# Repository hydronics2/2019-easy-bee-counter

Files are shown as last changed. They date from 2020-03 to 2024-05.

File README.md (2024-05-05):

# 2019 Easy Bee Counter V.1

This version of the bee counter is easy to solder and assemble (all through-hole).  It's been tested and works* with sample code provided.

The current tested design is easy to program and approachable to beginner programmers.  The printed circuit board accepts multiple Arduino platforms made by Adafruit including their line of [Adafruit Feather](https://www.adafruit.com/category/777) type micro-controllers and [Adafruit ItsyBitsy](https://www.adafruit.com/category/1008) micro-controllers.   The Adafruit feathers include wifi and long range radio features (*~~esp8266~~, esp32, and **LoRA). All the ItsyBitsy 3V models (M0, M4, and 32u4) should work fine.

*the esp8266 is missing A5 so you have to jumper to another pin
**see below issue with SPI

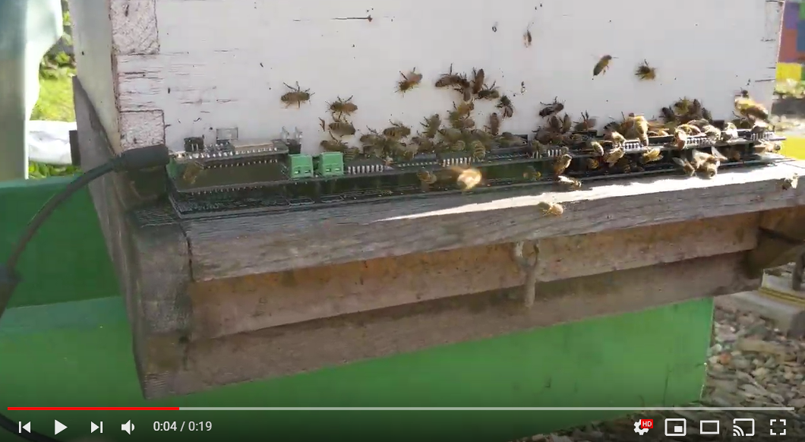
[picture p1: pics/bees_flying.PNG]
Foo (https://youtu.be/SzXWWUh2k8w)


### [Data Analysis - *why count bees?](https://github.com/hydronics2/2019-easy-bee-counter/blob/master/Data/README.md)
### [Instructions](https://github.com/hydronics2/2019-easy-bee-counter/blob/master/instructions/README.md)
### [Arduino Code](https://github.com/hydronics2/2019-easy-bee-counter/blob/master/arduino/README.md)
### Major Differences/Improvements
- All through-hole components for easy soldering
- Dual footprint, socketed, off-the-shelf micro-controllers => Feather and ItsyBitsy
- Program in Arduino, Lua, and microPython
- A total of 24 gates, 48 sensors, 6 shift registers
- ~14.75" long stretching the entire opening of a langstroth hive for easy placement
- using 2 PCBs to create a sandwich is an inexpensive quick solution. The PCBs must be ordered [black](https://github.com/hydronics2/2019-easy-bee-counter/tree/master/instructions/ordering_instructions) so the IR LED emitter is absorbed into the material.
- using 6 pin headers to create the turn-styles or gates
- N-Ch mosfet controlled IR LEDs such that LEDs can be controlled ON for short periods during while sensing (~75us). Allows for reduced power to less than 1ma (plus micro-controller).
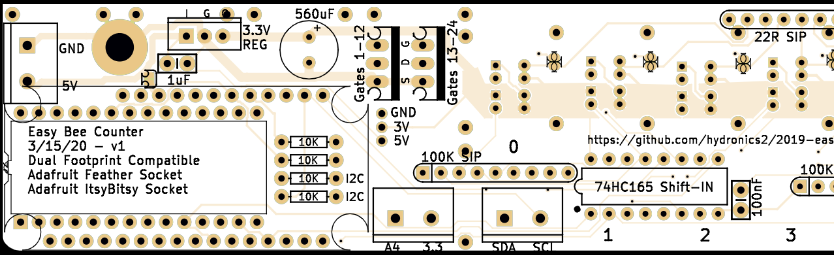
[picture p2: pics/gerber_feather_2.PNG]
feather

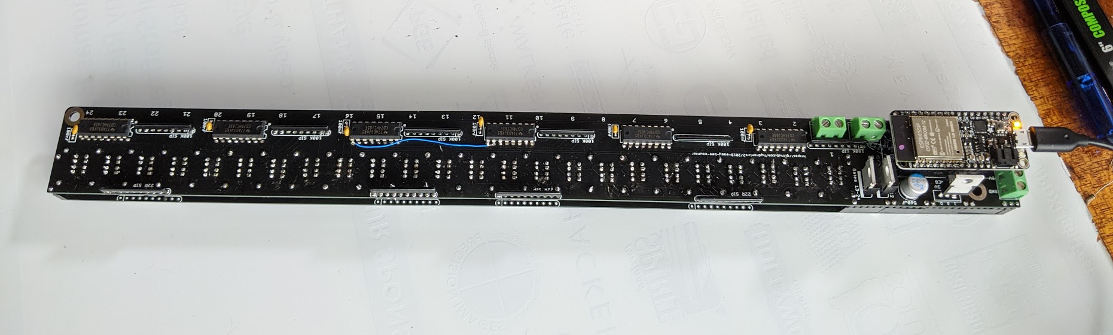
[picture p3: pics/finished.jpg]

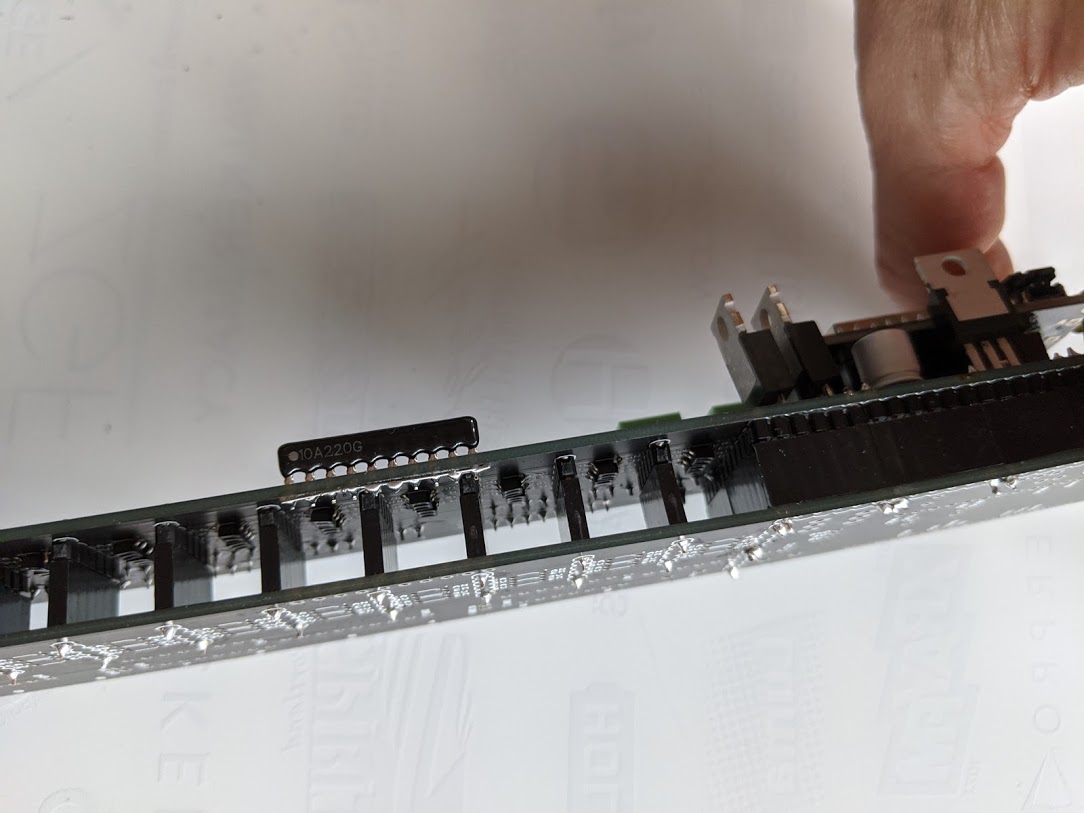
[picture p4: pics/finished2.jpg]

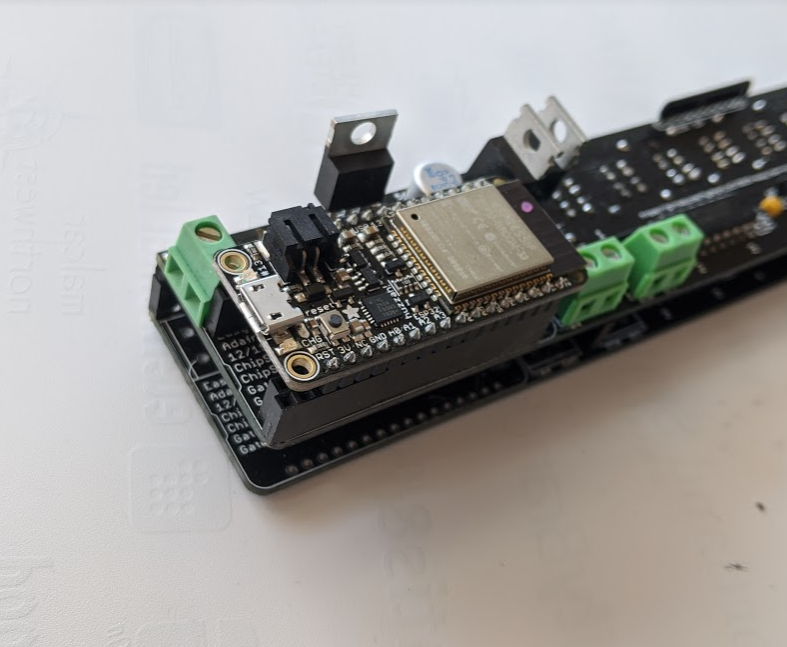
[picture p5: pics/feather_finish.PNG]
feather

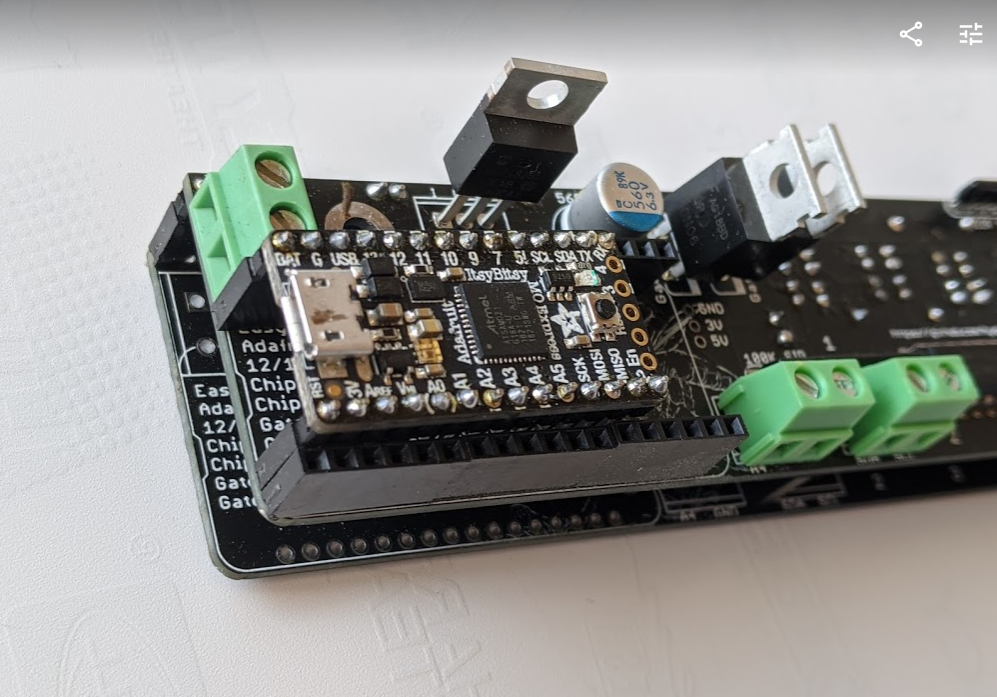
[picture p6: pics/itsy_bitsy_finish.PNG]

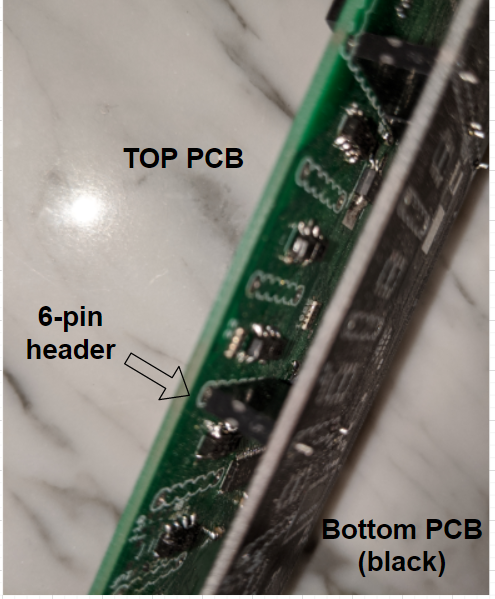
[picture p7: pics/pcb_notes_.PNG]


### General Operation
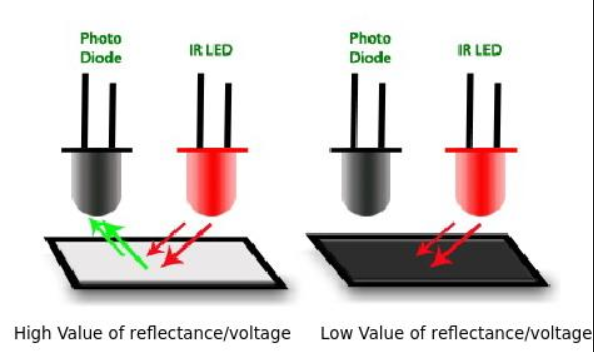
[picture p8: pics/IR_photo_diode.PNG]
https://github.com/hydronics2/2019-easy-bee-counter/blob/master/pics/IR_photo_diode.PNG
Honeybees are forced through 24 gates where optical sensors (48 sensors) determine whether the bee is present and determine the direction of the bee movement. Each optical sensors has an IR LED and an IR sensor. If no bee is present the IR light is absorbed into the black surface. If a bee is present the IR light reflects off the bee and triggers the sensor. 

### Micro-Controller Pinout
#### Feather ESP32 Pinout
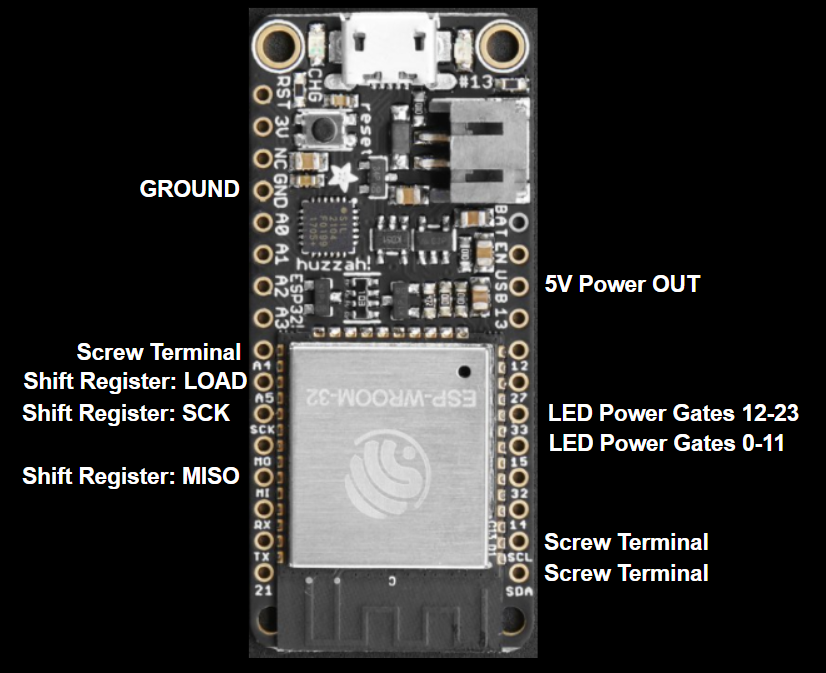
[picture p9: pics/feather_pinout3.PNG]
feather

#### ItsyBitsy Pinout
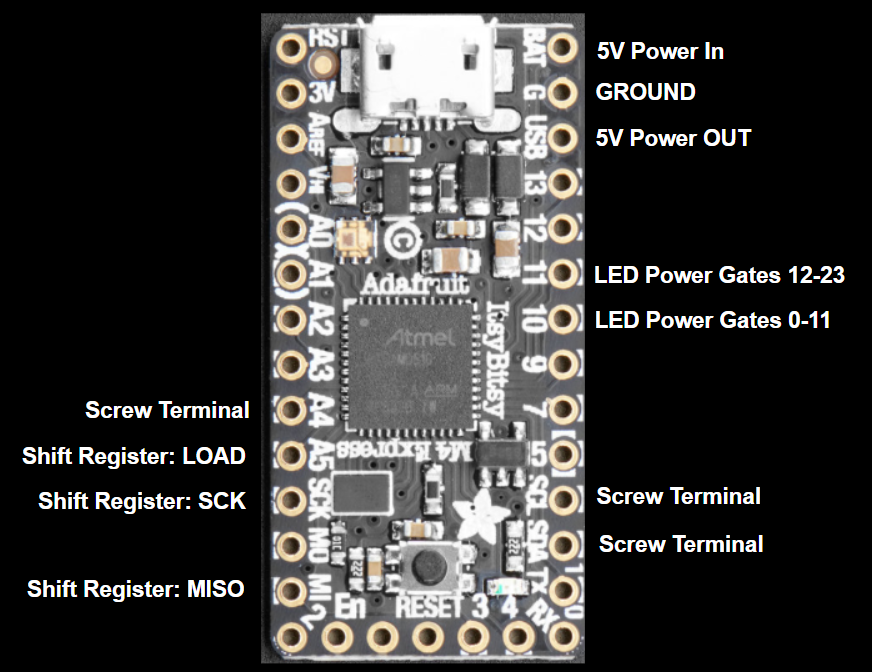
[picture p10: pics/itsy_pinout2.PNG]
itsy

### Shift-in registers
There are 6 shift-in registers. Here's a great description for how to connect and program [shift registers](http://www.gammon.com.au/forum/?id=11979).  The micro-controller's SPI pins read the shift registers. All six shift registers are read at the same time. The sensors are normally pulled low and show 3.3V or HIGH when a transistor is triggered and a bee is present.

Unfortunately the shift registers we're using (the most popular shift register chip!) are not [full SPI devices](https://electronics.stackexchange.com/questions/121249/how-to-put-a-74hc165-on-an-spi-bus) and wont share the SPI with other devices.. They're like the worst SPI devices!... therefore some boards like the Adalogger or LoRa just wont work out of the box. You can still do it by cutting some traces and patching the SPI lines to free pins and bitbanging the SPI to the shift registers.. buy yeah not optimum. You can get a true-spi shift register but the pinout will be different than the 74hc165 used here.

### IR LEDs
The 48 LEDs are divided into two sets of 24 with each set controlled by an N-ch mosfet. The normal forward voltage of each IR LED is 1.2V and about 20ma as shown on the [data sheet](https://www.sparkfun.com/datasheets/Robotics/QR_QRE1113.GR.pdf). Two LEDs are connected in series with a 22ohm resistor. There are jumpers on the board that allow the LEDs to bypass the current limiting resistors. Do not solder the jumper until fully tested! Refer to [these instructions](https://github.com/hydronics2/2019-easy-bee-counter/tree/master/instructions)

### Power
The PCB design connects the USB power pin from the uController to the 3.3V regulator so that a usb cable connected to the micro-controller can power the entire project.

### Bill of Materials
#### uController
The code was tested with the feather esp32 Huzzah and itsyBitsy M0 but will work with all these boards.
- feather Huzzah from [mouser](https://www.mouser.com/ProductDetail/485-3591)
- feather esp8266 from [mouser](https://www.mouser.com/ProductDetail/485-2821)
  - the esp8266 is missing A5, so if this micro is used you have to jumper to another pin
- feather LoRa 900mhz from [mouser](https://www.mouser.com/ProductDetail/485-3178)
- ItsyBitsy M0 from [mouser](https://www.mouser.com/ProductDetail/485-3727)
- ItsyBitsy M4 from [mouser](https://www.mouser.com/ProductDetail/485-3800)
#### PCB
[JLCPCB](https://jlcpcb.com/quote#/) ~$16-25 with shipping. Order the PCBs Black. See [these instructions](https://github.com/hydronics2/2019-easy-bee-counter/tree/master/instructions/ordering_instructions) for ordering.
#### Parts and Pieces from [mouser](https://www.mouser.com/ProjectManager/ProjectDetail.aspx?AccessID=054286973a)
See alternative pricing below for cheaper options specifically for the reflectance sensors.
- [qre1113 Reflective Sensors](https://www.mouser.com/ProductDetail/512-QRE1113f) qty(48)
- [6 pin female headers](https://www.mouser.com/ProductDetail/437-8018700610001101) 7mm high, 0.1" spacing, qty(~36)
- [22ohm resistors](https://www.mouser.com/ProductDetail/Xicon/266-22-RC?qs=sGAEpiMZZMvrmc6UYKmaNXFefT4dxyTCwtpTxTI0yoo%3D), bussed, qty(4)
SIP Packaged, bussed
- [100k ohm resistors](https://www.mouser.com/ProductDetail/IRC-TT-Electronics/L091S104LF?qs=sGAEpiMZZMvrmc6UYKmaNdnTrsZX%2FuSiyGduauH5Qpc%3D) bussed, qty(6)
SIP-9, 8 resistors, 9 pins
- Shift registers, qty(6)
[74HC165](https://www.mouser.com/ProductDetail/595-SN74HC165N)
- [3.3V Regulator](https://www.mouser.com/ProductDetail/Microchip-Technology/MCP1826S-3302E-AB?qs=sGAEpiMZZMsGz1a6aV8DcJ7KfjtCj7Xd5CqQpyOghgk%3D), (input, ground, output - IGO, pinout), qty(1)
- [screw terminals](https://www.mouser.com/ProductDetail/490-TB006-508-02BE) Two pin, 0.1", qty(3)
- [0.1 uF Ceramic Capacitor](https://www.mouser.com/ProductDetail/594-K104K15X7RF53H5), through hole, qty(6)
- [1 uF Ceramic Capacitor](https://www.mouser.com/ProductDetail/594-K105Z20Y5VF5TL2), through hole, qty(1)
- [560uF, 6.3V Capacitor](https://www.mouser.com/ProductDetail/661-APSC6R3L561MH08S)
low esr, 3.5mm lead spacing, 8mm diameter
- N-Channel Mosfet [FQP30N06](https://www.mouser.com/ProductDetail/512-FQP30N06L), qty(2)
  - [chinswain](https://github.com/hydronics2/2019-easy-bee-counter/issues/20#issuecomment-2094117078) suggested using this IRLB8721PbF N-Channel mosfet. He suggested the signal threshold of 3.3V was not sufficient to meet the gate threshold for the FQP30N06L... and it could be the ebay versions of the FQP30N06L floating around are not to spec.

#### Alternative pricing from Chinese distributor LCSC
Someone pointed out some alternative pricing that can really bring the cost down.
- [ITR8307 Reflectance Sensors](https://lcsc.com/product-detail/Photo-Interrupter_Everlight-Elec-ITR8307_C63451.html) ~$0.13/each @ qty(48) (same as QRE1113)
- [6 pin female headers](https://lcsc.com/product-detail/Pin-Header-Female-Header_BOOMELE-Boom-Precision-Elec-C40877_C40877.html) 8.5mm high. ~$0.05/each @ qty(36+)
- [22 ohm SIP](https://lcsc.com/product-detail/Resistor-Networks-Arrays_FH-Guangdong-Fenghua-Advanced-Tech-A09-220JP_C9105.html) 8 resistor, 9 pin, it will fit. $0.44 for qty(4)
- [100k SIP Resistors](https://lcsc.com/product-detail/Resistor-Networks-Arrays_FH-Guangdong-Fenghua-Advanced-Tech-A09-104JP_C9108.html) 8 resistor, 9pin, it will fit. $0.44 for qty(6)

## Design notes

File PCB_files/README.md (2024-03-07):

## Printed Circuit Board (PCB)

This PCB version has two footprints that accept the wider (0.8") Adafruit Feather micro-controllers such as the [esp32](https://www.adafruit.com/product/3405) and the narrower (0.6")[Adafruit ItsyBitsy](https://www.adafruit.com/category/1008) micro-controllers.

**UPDATE** The GERBER files were developed from the kicad board files so had to remove the gerber files. You now have to use the Eagle board files or generate gerber files from the eagle board files.... or a lot of PCB manufacturers will take eagle PCB files and you don't have to generate your own gerber files. You can still use the kicad files but you have to route a small trace for the SCK pin. See this bug report: https://github.com/hydronics2/2019-easy-bee-counter/issues/25 

feather

These files were created in Autocad EAGLE PCB software. The zipped files are the gerber files needed by the PCB manufacturer.

Right click and 'save link as' to download the files and then upload them to the PCB manufacturer. See the [ordering instructions here](https://github.com/hydronics2/2019-easy-bee-counter/tree/master/instructions/ordering_instructions). Most board shops require a minimum order of 3-5 boards and you'll need 2 boards to sandwich together to complete one bee counter.

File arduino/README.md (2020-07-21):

# Arduino

There are three arduino scripts attached.
- Blink_IR_leds.ino - used to visually inspect LEDs working
- test_shift_registers.ino - used to functionally test sensors
- bee_counting.ino - used to count bees!

### Warning
Soldering the 24 jumpers increases the throw range of the IR sensors by increasing the forward voltage and current in the LED. This is fine if we keep the LEDs ON time to less than 100us. This is described in the [data sheet](https://www.sparkfun.com/datasheets/Robotics/QR_QRE1113.GR.pdf).

Two scripts above, both [test_shift_registers](https://github.com/hydronics2/2019-easy-bee-counter/blob/master/arduino/test_shift_registers/test_shift_registers.ino) and [bee_counting](https://github.com/hydronics2/2019-easy-bee-counter/blob/master/arduino/bee_counting/bee_counting.ino) satisfy this requirement by only turning the LEDs ON for 75us.  This is shown on line 68 (shift register) and line 158 (bee_counting). Following the ON time there is a delay of ~15-20ms before turning them ON again which preserves the life of the LED.

### Calibrating the Bee Counter
I've captured some amazing data over the years. It's possible to calibrate the bee counter to achieve the required repeatability. Some of the obstacles to calibrate for include:
 - although bees don't add propolis to sensors they will spend several days filling voids with propolis upon initial installation
 - bearding in the summer evenings and general guard bees mulling about give false triggers
 - direct sun light at a low angle will false trigger sensors (this can be mitigated pretty easily)

One method is to measure the speed of the bees movement and only count known movements and throwing out all false triggers. This method misses a lot of bees but can give consistent values. It takes a bee about 180-350ms to traverse the sensor region.

The [bee_counting](https://github.com/hydronics2/2019-easy-bee-counter/blob/master/arduino/bee_counting/bee_counting.ino) code measures the speed of the bees through the sensor and counts bees moving faster than 650ms and demands the time between finishing one sensor and finishing the 2nd sensor is less than 150ms.

### Micropython

@jin4 contributed the python code that ran successfully on a pycom device... "This code runs on a pycom device, but i think the code will work on any micropython device since the imports are not pycom specific."

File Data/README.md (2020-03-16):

# Possible Uses
- the rate of expansion or decline of bee flights might indicate hive health
- the expansion or decline of orientation flights over days might signal queen health
- the time shift between peaks of bees leaving and returning might indicate number of foragers and distance to pollen/nectar source.
- comparison between two or move hives to test for manipulations; such as,
  - adding/removing honey supers
  - internal sugar syrup feeding
  - oxalic acid mite treatments
- honey bee education or museum type installation
- introduction to electronics, soldering and micro-controller programming

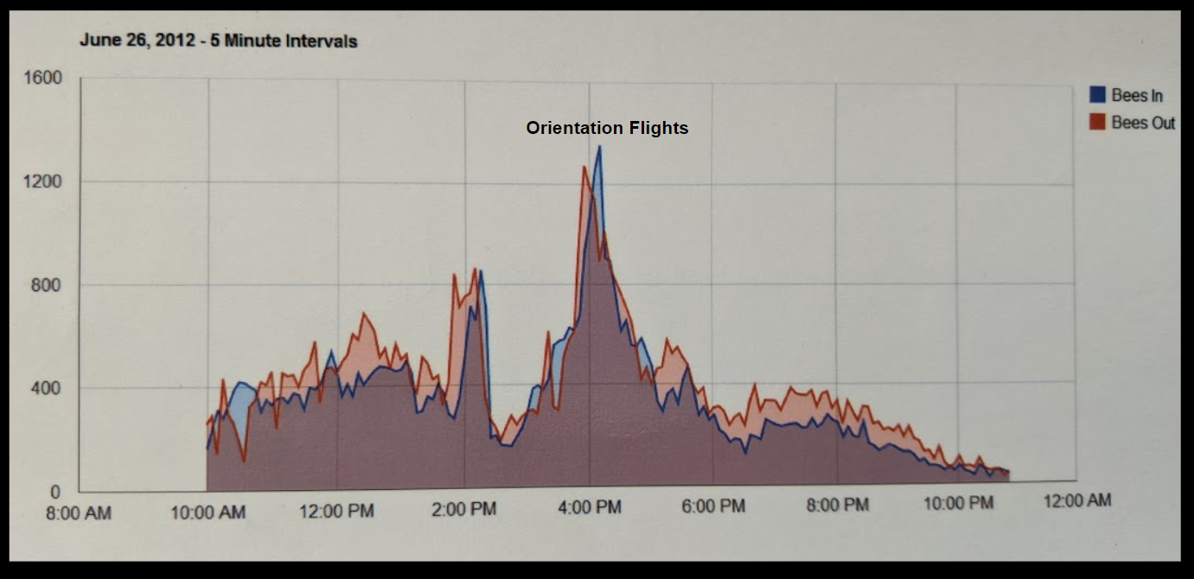
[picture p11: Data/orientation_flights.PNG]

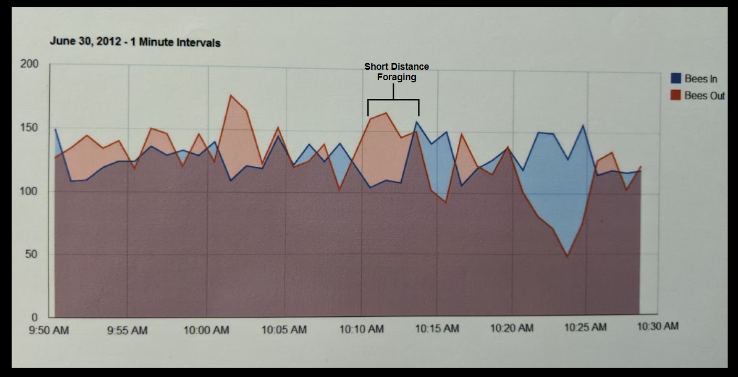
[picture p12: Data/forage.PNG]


## Hive health
Equating bee flight data and orientation flights to over all hive health or queen health seems possible. Orientation flights is a behavior of 'middle aged' bees about [20 days old](https://www.arnia.co.uk/honey-bee-orientation/#). Before foraging bees of this age will leave the hive as a group at around mid day resulting in an easy to see ~45min peak in data.

If there is a drop in orientation flights it might indicate a reduction in egg laying ~42 days prior (22 days hatch + 20 days till forage).

## Foraging distance
It's easy to see small but distinct shifts between bees OUT and bees IN. This indicates both a volume of bees that are leaving and returning together as well as a rough distance or time to the foraging location.

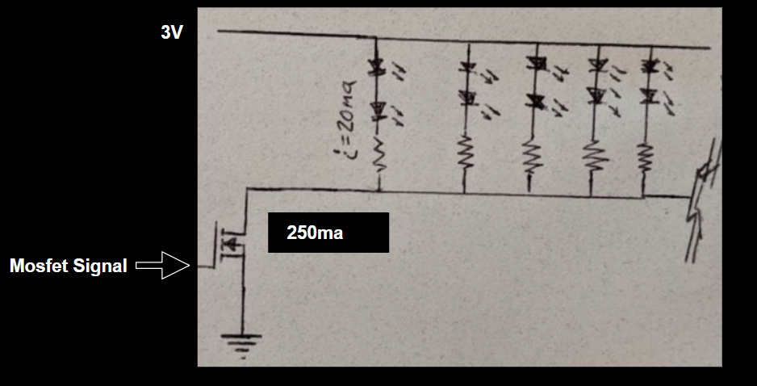
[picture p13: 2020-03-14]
pics/led_schematic.PNG

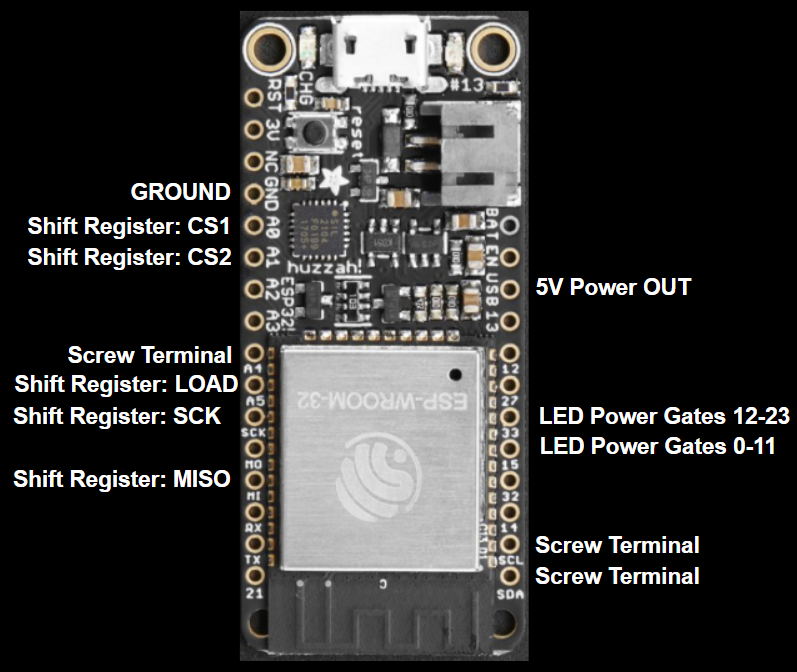
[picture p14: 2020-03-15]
pics/feather_pinout2.PNG

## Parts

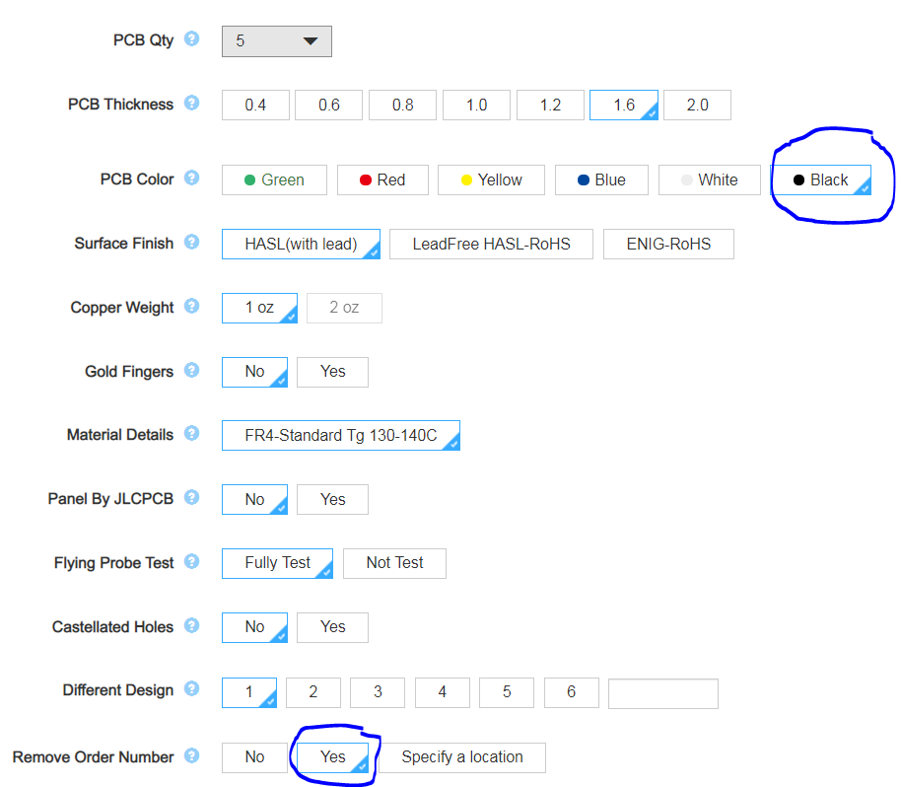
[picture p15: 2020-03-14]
pics/JLCPCB_order.PNG

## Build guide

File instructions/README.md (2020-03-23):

# 2019 Easy Bee Counter V.1 Build Instructions

This version of the bee counter is all through hole components. It's easy to solder and assemble. This is the 2nd version of the board (V1) completed March 2020. If you got the [Version 0](https://github.com/hydronics2/2019-easy-bee-counter/tree/b06d461f1881f2709d81f82d817dc76170a77fa7) board (Jan/Feb 2020) you just have to fix some of my previous mistakes including adding a jumper wire shown [here](https://github.com/hydronics2/2019-easy-bee-counter/blob/master/instructions/archive)

1) Install IR sensors - [QRE1113](https://www.mouser.com/ProductDetail/512-QRE1113f) or [ITR8307](https://lcsc.com/product-detail/Photo-Interrupter_Everlight-Elec-ITR8307_C63451.html)

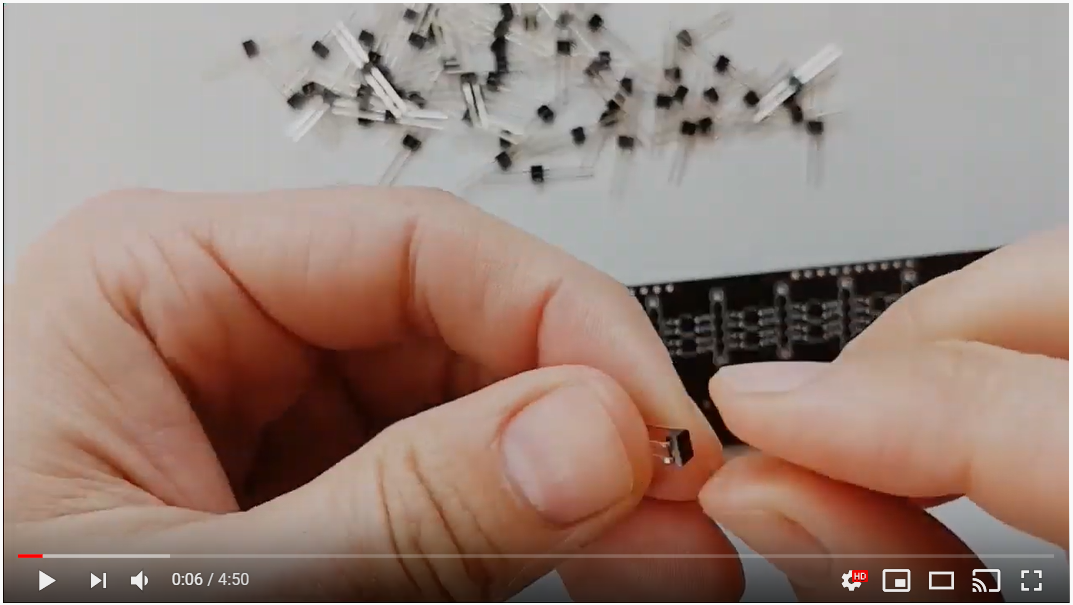
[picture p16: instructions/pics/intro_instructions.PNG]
(https://youtu.be/Xx23OmlHwkE)


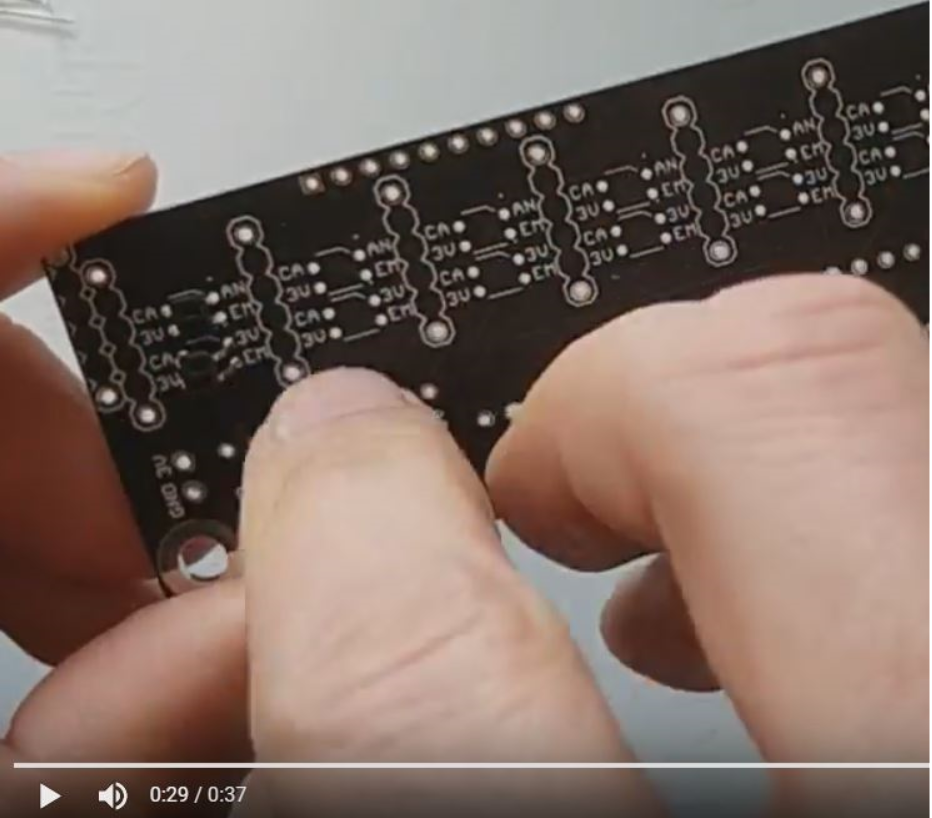
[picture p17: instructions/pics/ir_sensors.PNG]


2) install shift registers qty(6), SIP 22R LED resistors and 100k pulldown resistors.
- Shift registers, qty(6) [74HC165](https://www.mouser.com/ProductDetail/595-SN74HC165N)
- [22ohm resistors](https://www.mouser.com/ProductDetail/Xicon/266-22-RC?qs=sGAEpiMZZMvrmc6UYKmaNXFefT4dxyTCwtpTxTI0yoo%3D), bussed, qty(4)
SIP Packaged, bussed
- [100k ohm resistors](https://www.mouser.com/ProductDetail/IRC-TT-Electronics/L091S104LF?qs=sGAEpiMZZMvrmc6UYKmaNdnTrsZX%2FuSiyGduauH5Qpc%3D) bussed, qty(6)
SIP-9, 8 resistors, 9 pins

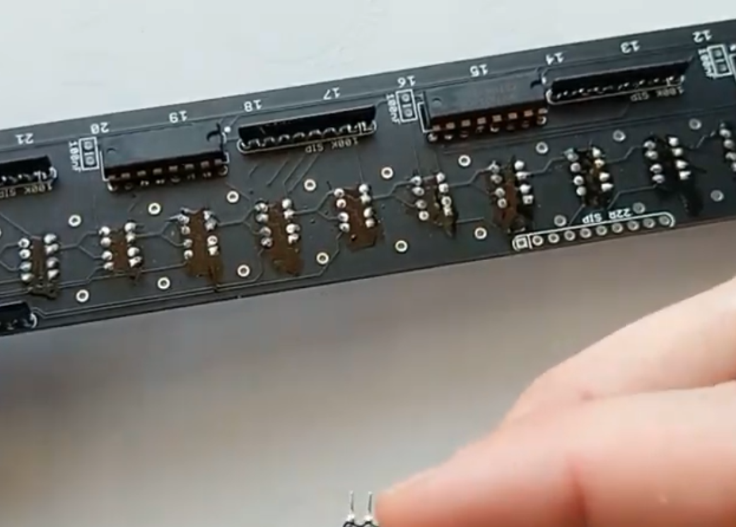
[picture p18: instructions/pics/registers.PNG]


3) install power mosfets qty(2),
- N-Channel Mosfet [FQP30N06](https://www.mouser.com/ProductDetail/512-FQP30N06L)

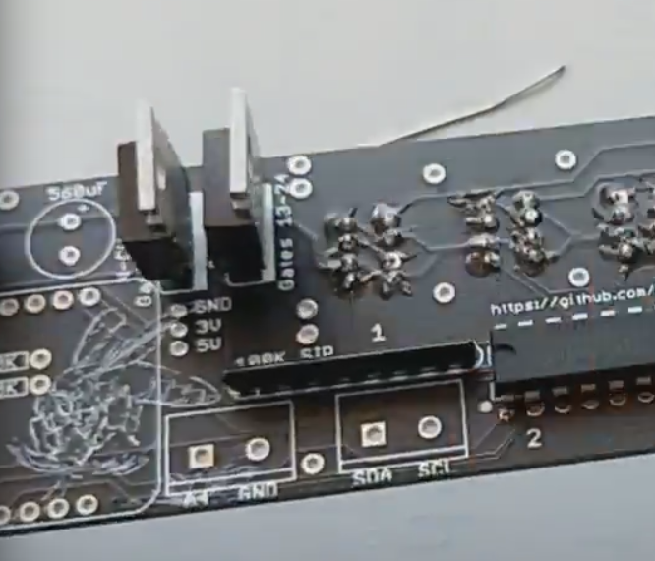
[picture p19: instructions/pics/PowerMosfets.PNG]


4) install small capacitors

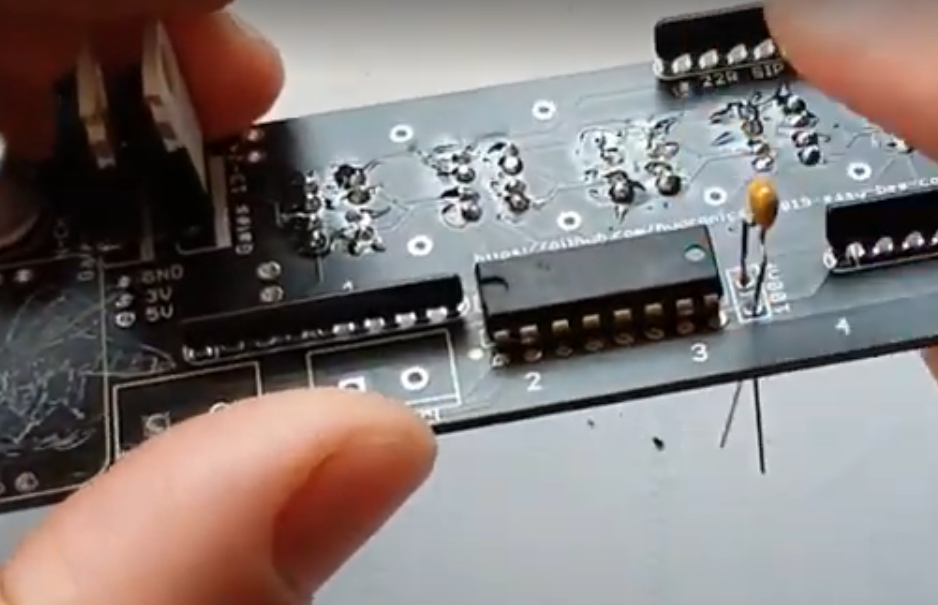
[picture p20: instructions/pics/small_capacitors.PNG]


5) place/solder 3.3V power regulator

- [3.3V Regulator](https://www.mouser.com/ProductDetail/Microchip-Technology/MCP1826S-3302E-AB?qs=sGAEpiMZZMsGz1a6aV8DcJ7KfjtCj7Xd5CqQpyOghgk%3D), (input, ground, output - IGO, pinout), qty(1)

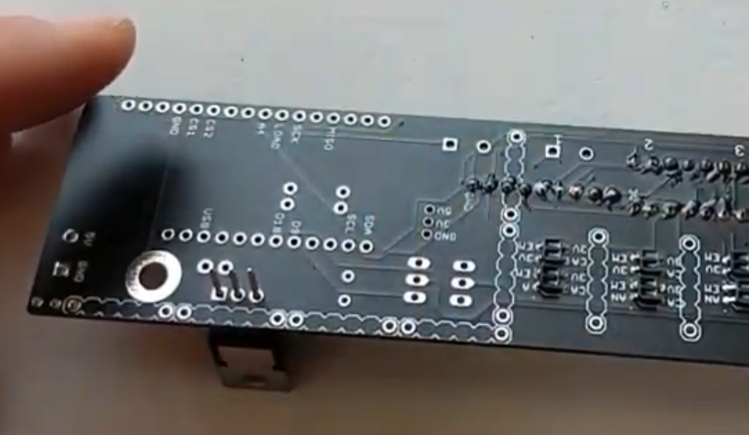
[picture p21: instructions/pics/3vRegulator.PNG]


6) install large Capacitor

- [560uF, 6.3V Capacitor](https://www.mouser.com/ProductDetail/661-APSC6R3L561MH08S)

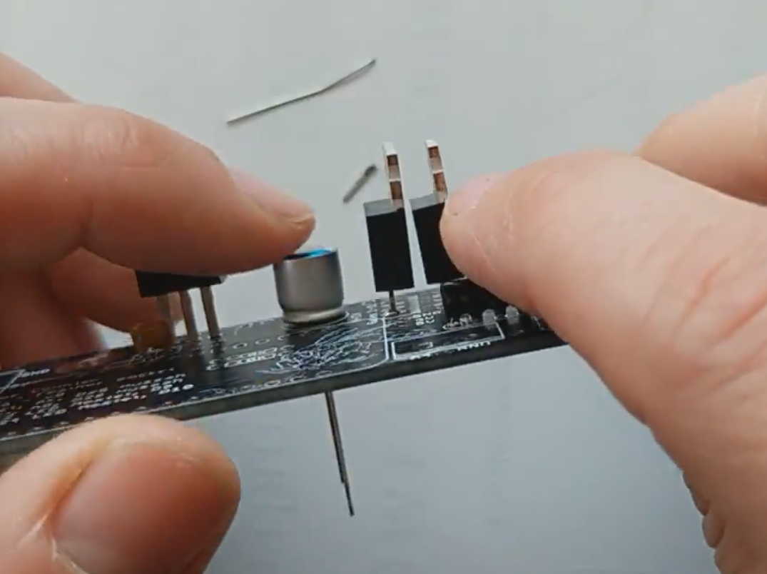
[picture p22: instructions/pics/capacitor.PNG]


7) install green screw terminals, qty(3)

- [screw terminals](https://www.mouser.com/ProductDetail/490-TB006-508-02BE) Two pin, 0.1", qty(3)

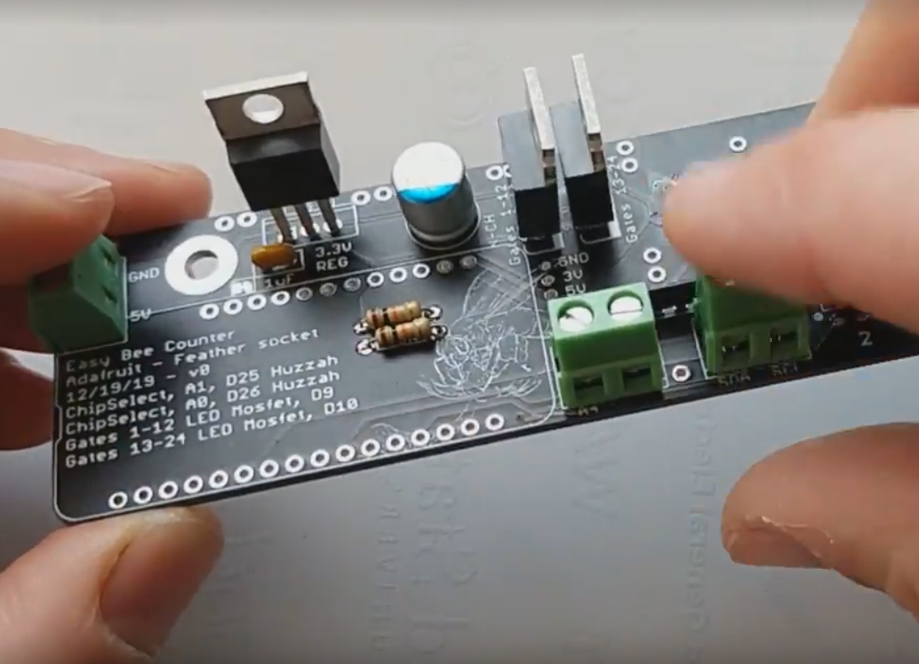
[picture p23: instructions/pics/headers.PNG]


8) install headers for microprocessor

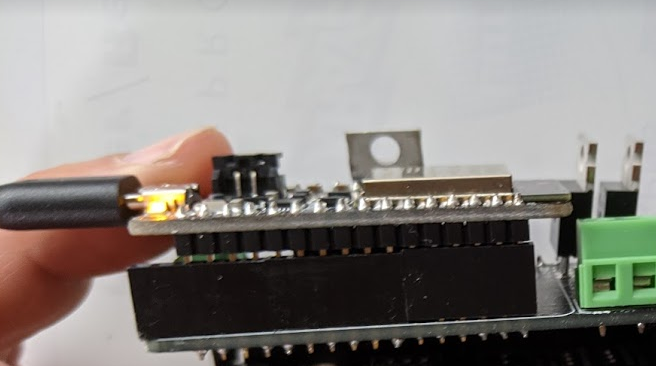
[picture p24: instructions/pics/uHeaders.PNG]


9) install qty(4) 10K Resistors (picture is wrong.. only shows 2 resistors)
- i2c pullup resistors
- pulldown resistors for power mosfets

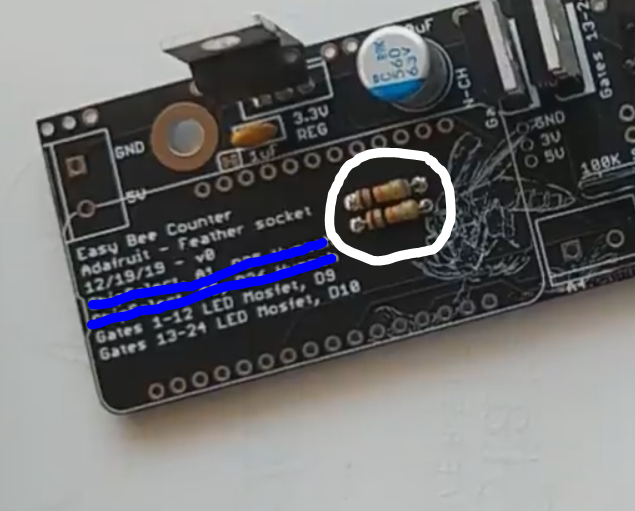
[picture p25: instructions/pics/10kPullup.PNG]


## TEST sensors
Before you go any farther, test all your LEDs/sensors! It's much easier to test these now before going further.
Run the sample code [blink_IR_Leds](https://github.com/hydronics2/2019-easy-bee-counter/blob/master/arduino/Blink_IR_Leds/Blink_IR_Leds.ino).

The IR LEDs are invisible to the human eye but many phones and cameras allow you to see the IR LEDs. See picture. (unfortunately most iphones have IR filters so try another phone until you see IR leds). This step is very important so make sure you can see all the LEDs.

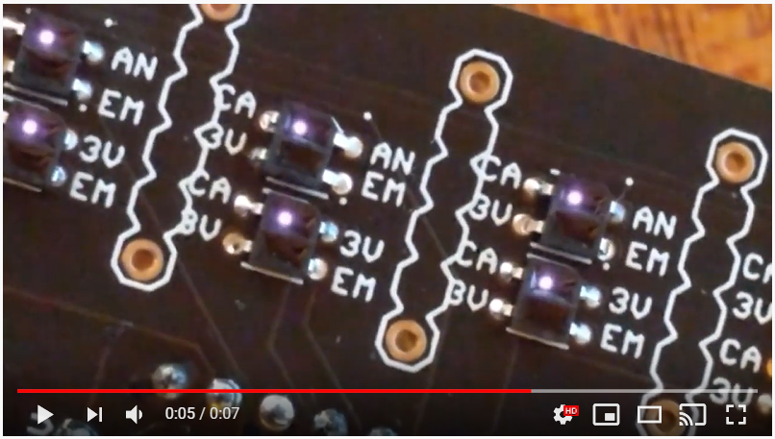
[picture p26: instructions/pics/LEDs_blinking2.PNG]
(https://youtu.be/hH9fQr7Om6E)


LEDs look good? If no LEDs are blinking? Check to make sure you have 3.3V on the 3.3V pin header. If one or two LEDs are out, reflow your pins and/or replace the LEDs until you get 100% LEDs blinking together.

LEDs good, great, next test the shift registers with the sample code [test_shift_registers](https://github.com/hydronics2/2019-easy-bee-counter/blob/master/arduino/test_shift_registers/test_shift_registers.ino). Use a white piece of paper to trigger the sensors. If some sensors are not working, check your pins, heat up and reflow solder on pins as needed.

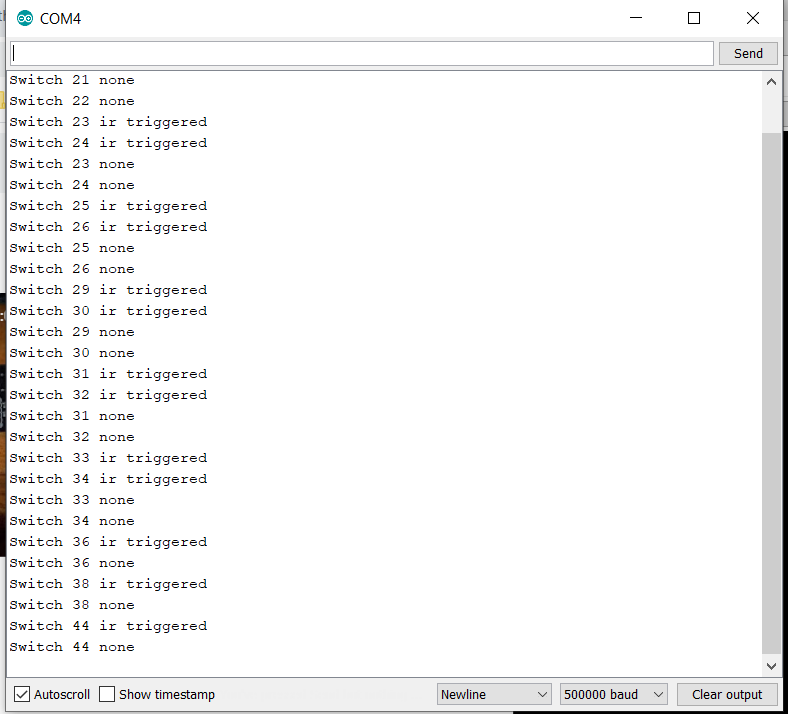
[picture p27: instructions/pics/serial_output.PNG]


10) Finish assembly once all sensors are tested. Install the headers that connect the top PCB to the bottom PCB.

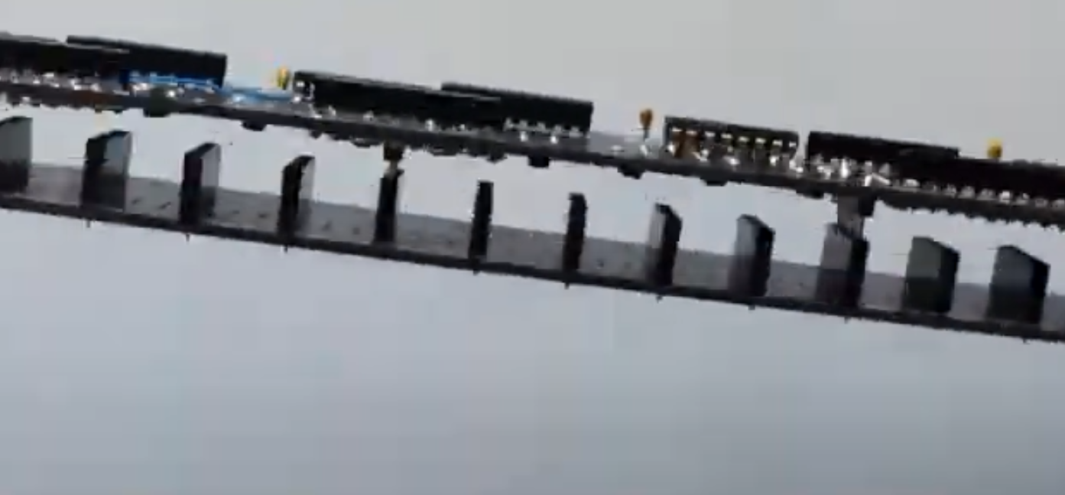
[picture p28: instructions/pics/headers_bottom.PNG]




11) Ok, once everything is tested out, you can solder these jumpers.... Soldering the 24 jumpers increases the throw range of the IR sensors by increasing the forward voltage and current in the LED. This is fine to do if we keep the LEDs ON time to less than 100us.

Two scripts provided, both [test_shift_registers](https://github.com/hydronics2/2019-easy-bee-counter/blob/master/arduino/test_shift_registers/test_shift_registers.ino) and [bee_counting](https://github.com/hydronics2/2019-easy-bee-counter/blob/master/arduino/bee_counting/bee_counting.ino) satisfy this requirement by only turning the LEDs ON for 75us.  This is shown on line 68 (shift register) and line 158 (bee_counting).

Solder all 24 of the jumpers.
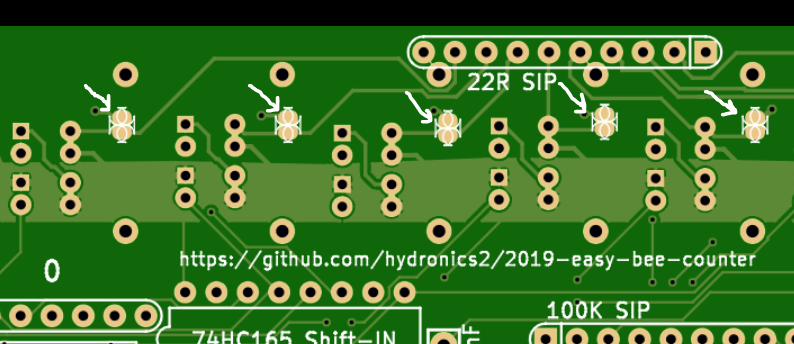
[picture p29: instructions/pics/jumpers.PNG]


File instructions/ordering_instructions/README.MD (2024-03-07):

## Ordering from JLCPCB

There are a lot of different PCB manufacturers to choose from. These instructions show JLCPCB. You need a manufacturer that can make black PCBs if you want to use the PCBs to make a sandwich. The IR LEDs/sensors need to point to a black surface to prevent false triggers, so the bottom PCB has to be black.

1. Download the entire repo... hit the large green button that says "clone or download" [github](https://github.com/hydronics2/2019-easy-bee-counter)... navigate to the Eagle_v0.2 file. These are the PCB files. Do not use the kiCad files as there is a missing trace for the SCK pin for the itsybitsy footprint.
2. Go to [JLCPCB.com](https://jlcpcb.com/quote#/), create an account and click the ORDER NOW button.
3. Add your PCB files.
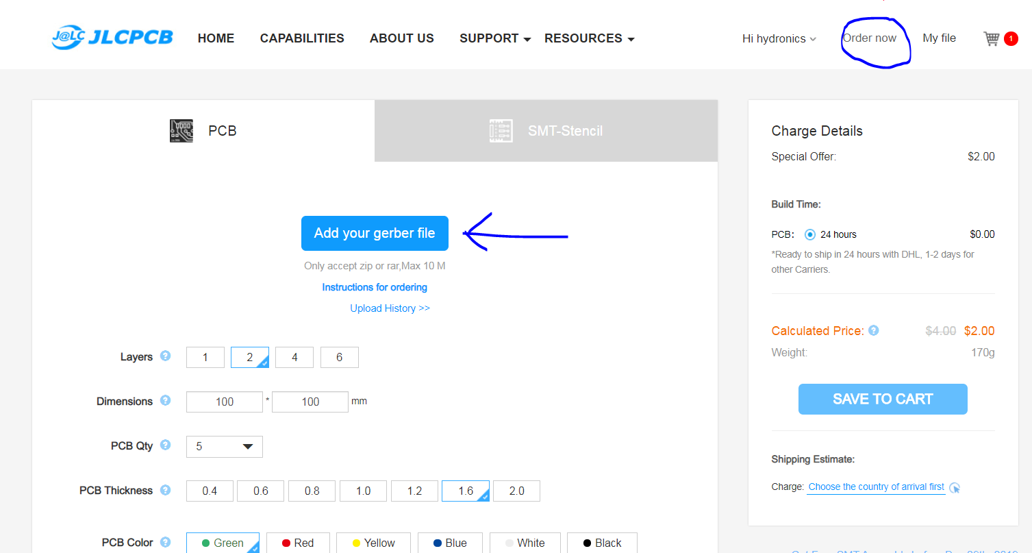
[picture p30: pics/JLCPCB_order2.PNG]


4. Select 'Black' as the PCB color.  Also for "Remove Order Number", select YES
[pic](https://github.com/hydronics2/2019-easy-bee-counter/blob/master/pics/JLCPCB_order.PNG)

The cost is about $8 for a minimum order of qty(5) PCBs plus $9-16 shipping depending on method.

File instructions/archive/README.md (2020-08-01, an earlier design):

# 2019 Easy Bee Counter V.0 Build Instructions

I made a few mistakes on the first version (v0). The 74hc165 is not a true SPI device. It doesn't have a tri-state buffer on the MISO.

https://electronics.stackexchange.com/questions/121249/how-to-put-a-74hc165-on-an-spi-bus

The following fix, allows you to shift in all the data at once (all shift registers)... all shift registers are therefore always enabled. This fix wil work with all the stand alone feather micro-controllers... ESP32, ESP8266, SAMD21 M0 and M4... but doesn't work with the [LoRa module](https://cdn-learn.adafruit.com/assets/assets/000/031/658/original/feather_schem.png?1460518302) as it ALSO uses the SPI buss. In order to work with the LORa module you need to swap out the 74hc165 shift registers with true SPI based shift registers... like the 74HC589 referenced in the above [stack exchange](https://electronics.stackexchange.com/a/128220) answer.

To fix the old board... we want to read all 6 shift registers so just cut one of the MISO signal lines and add a jumper.

video cutting signal https://photos.app.goo.gl/VkyV412uJGBNS7sx8

video adding jumper https://photos.app.goo.gl/QXMhvH7FzpDfXWLs7

Top view showing cut jumper
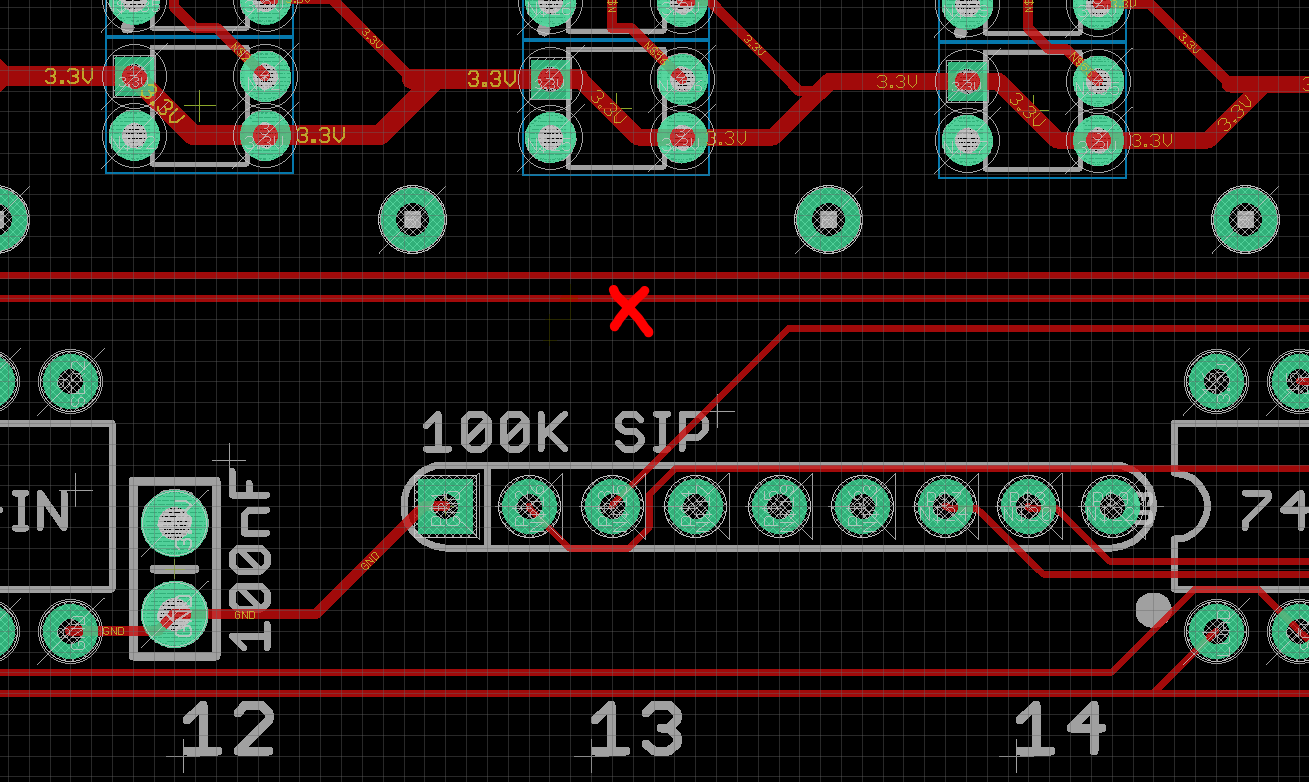
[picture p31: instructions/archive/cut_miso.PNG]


Top view showing jumper(blue)
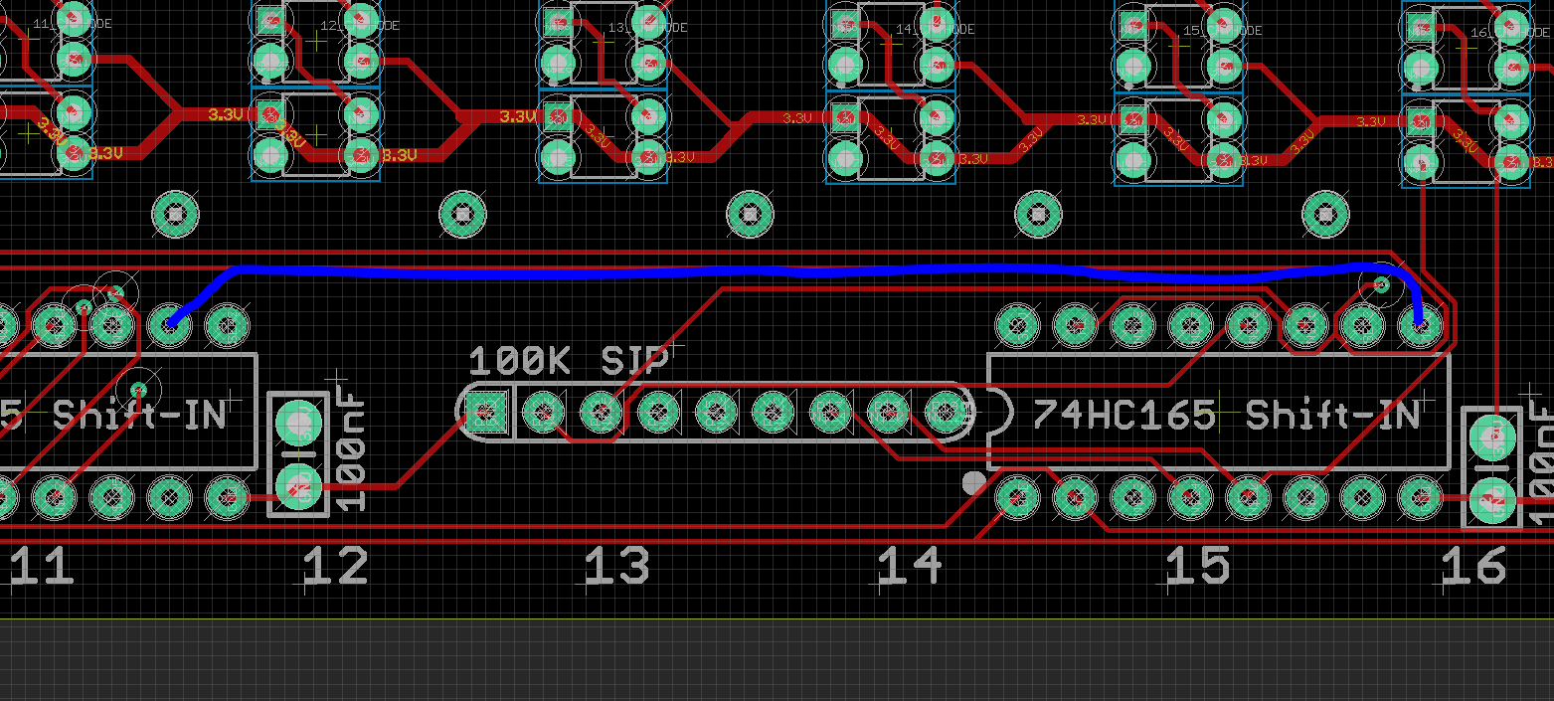
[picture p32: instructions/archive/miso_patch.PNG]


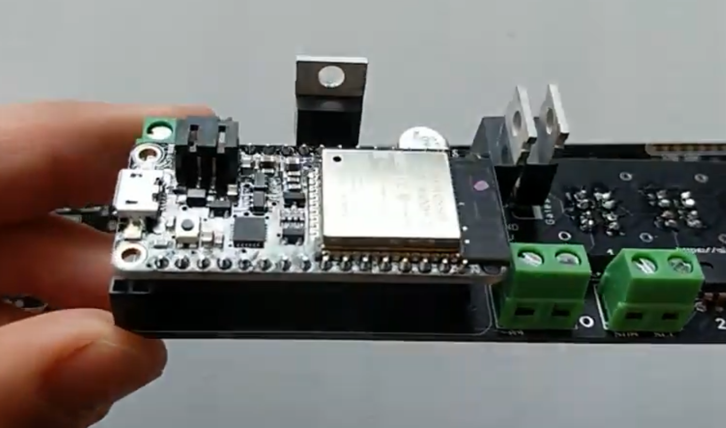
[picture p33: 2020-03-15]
instructions/pics/ucontroller_w_headers.PNG

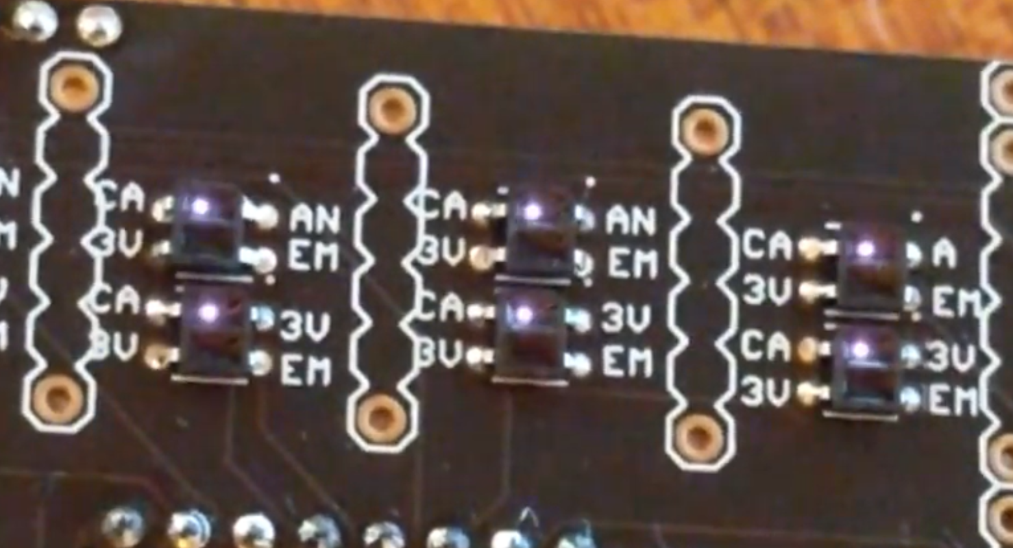
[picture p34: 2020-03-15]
instructions/pics/ir_sensors_on.PNG

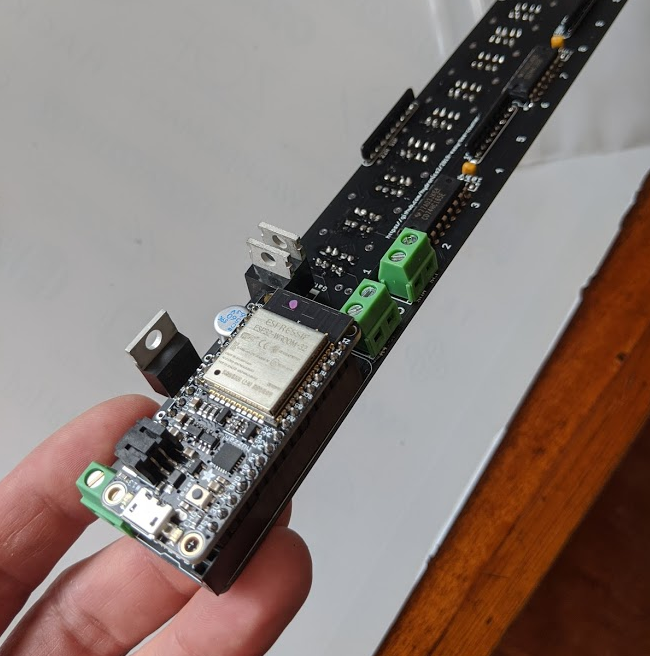
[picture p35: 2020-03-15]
instructions/pics/ucontroller_w_headers2.PNG

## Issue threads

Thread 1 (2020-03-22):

hydronics2/2019-easy-bee-counter #1: Suggestion...

owendelong, 2020-03-22:
Any reason https://recom-power.com/pdf/Innoline/R-78-1.0.pdf wouldn't be a suitable (superior) replacement for the MCP1826S-3302E-AB?

Looks like the specs are basically identical, but this is a switcher instead of a linear, so it should be more efficient (less heat dissipation, less power input, etc.

I'm looking at possibly adding some hinges and servos to the ESP32 (or ESP8266, haven't fully decided yet) version to create a programmable entrance reducer and also inputs for a load cell to track hive weight (bee and honey production, time to add supers, etc.).

I'm thinking 12, 6, 3, 2, 1 wide doors, facilitating a wide range of entrance sizes.

Curious for any thoughts you might have on this idea.

owendelong, 2020-03-23:
So looking through things, you don't actually seem to use the screw terminals for anything... Is that correct? Is the 3v,A4 screw terminal intended for connecting a load cell?

It also appears you don't actually use the I2C connections for anything. Are they needed? Am I missing something?

Thanks in advance.

BTW, love the bee logo on the board.

hydronics2, 2020-03-23:
Yes! the screw terminals are for adding sensors too. Nothing identified but that's what they are for.

I agree load cells are super important for looking at hive health and activity. 

That's an interesting idea adding retractable entrance reducers. 

you bet, I like the idea of the drop-in-replacement mini switching power supply. Especially  for say reducing parasitic losses (?).

hydronics2, 2020-03-23:
Also, If you are digging into this... I'm missing the jumpers on this CAD version. Do you follow? They are in the gerber files. They jumper the LED resistors. Just a heads up. If you already ordered the board you can easily short the SIP resistors. [That's what I did on my first version. ](https://github.com/hydronics2/2019-easy-bee-counter/blob/master/PCB_files/Eagle_v0.2/shorted_SIP_resistors.png)

owendelong, 2020-03-24:
I haven’t ordered the board… I’ve just started analyzing it for modification (hinges and servos), so no worries there.

I haven’t even ordered the LED/Sensor units yet. (ordered pretty much everything else).

Still trying to figure out how I can “see” the IR LEDs in an all-Apple household.

I’m guessing I’ll end up with a 49th sensor on a separate AT328P with a cheap OLED display or such to use as a “scanner”.

Owen

hydronics2, 2020-03-24:
ha.. good luck. You can also use an old digital camera to see the IR leds.... if you still have one of those.

owendelong, 2020-03-24:
I’ll find something that works… If I do end up building a device and code that can be used to “scan” the LEDs, do you want me to contribute it to the repo?

hydronics2, 2020-03-25:
Sure, if you find it helpful. Thanks

owendelong, 2020-03-28:
Any chance you can provide me the eagle part for your resistor bypass jumpers?
(Either the name of the eagle library and part name, or, a copy of the part)?

I've been looking at the board and I found a few interesting things... I noticed that the sensors were kind of all over the place in the vertical. That seemed to make some routing a bit more challenging, so I aligned them all to 715 and 879, respectively. I also noticed that while the gate headers are on even 500 mil centers (5435, 5935, 6435, ...), the sensors are to the left and right of the 250 mil mark between the headers. I've re-centered those.

I also noticed a few pieces of left over routing cruft (bits of overlapping pieces of traces). Harmless, but created some odd line shapes when zoomed in close.

I'm working on rerouting the board now, hence it would be nice to get the jumpers you used to be able to place them in this process.

hydronics2, 2020-03-30:
Hey there, sorry for the delay getting back to you. I lost my access to Eagle Pro ( left my previous job) so I actually transitioned to kiCAD and added the jumpers in kiCAD..... soooo I don't have the eagle file for that jumper. I"m going to upload the kiCAD files.

owendelong, 2020-03-30:
OK... I used a pair of vias close together to hopefully do the same job. If I end up redoing it, I'll replace those with an 0204 0Ω resistor, which in hindsight is what I probably should have done in the first place).

owendelong, 2020-03-30:
I keep wanting to switch to kicad, but the learning curve seems steep and I have so many parts I've built in Eagle that it's hard to get over the hump.

hydronics2, 2020-04-01:
it wasn't as bad as I thought it would be. What really forced me to try it out was when I needed to make edits to this large board!... There's an import button in Kicad that easily (and seemingly accurate) method to import eagle files.  The other thing that works well on kicad is the 3d rendering.. Check out these renderings.. https://github.com/hydronics2/COVID-19-Airflow-Sensor-AFH55M12

Overall, Eagle has a much smoother interface. There's a lot of choppy zooming in and out in Kicad that is nerve racking...

owendelong, 2020-04-01:
> On Apr 1, 2020, at 11:02 , Thomas <notifications@github.com> wrote:
> 
> 
> it wasn't as bad as I thought it would be. What really forced me to try it out was when I needed to make edits to this large board!... There's an import button in Kicad that easily (and seemingly accurate) method to import eagle files. The other thing that works well on kicad is the 3d rendering.. Check out these renderings.. https://github.com/hydronics2/COVID-19-Airflow-Sensor-AFH55M12 <https://github.com/hydronics2/COVID-19-Airflow-Sensor-AFH55M12>
> 

Hmmm… I’ll have to give it another look… I don’t remember that being there last time I tried it out. Does that import work for library parts or just boards?

I was less worried about importing existing board designs and schematics (I don’t tend to make anything very complex) than I was about getting my library parts over.
> Overall, Eagle has a much smoother interface. There's a lot of choppy zooming in and out in Kicad that is nerve racking…
> 
The good news is that’s probably a combination of CPU power and optimization and among the easier things to fix (vs. fundamental flaws like exorbitant commercial
licensing fees, restrictive licensing, inability to move pin names in library parts, etc.).

Thanks,

Owen

owendelong, 2020-05-05:
So I've had to kind of back-burner this project for a bit. Still making some progress, but it's slow.

Still working in Eagle for now, but I agree those are some nice 3d renderings you pointed out.

One thing that drew me back into Eagle was the Fusion 360 integration (it's now a single license for the previous price of Eagle).

Any chance you could send me the QRE1113 library you used? I don't have it.

owendelong, 2020-05-05:
FYI, In the version I'm modifying, I've rewired the SIP resistors for the sense lines to make the board layout a little easier. (put them in order on the SIP pack to match the sensor placement).

hydronics2, 2020-05-06:
ok, I did a library export using ULP and put the libraries folder in with
the eagle files:
https://github.com/hydronics2/2019-easy-bee-counter/tree/master/PCB_files/Eagle_v0.2
FYI, I'm pretty sure I got those reflective sensors from the standard
Sparkfun library.

owendelong, 2020-05-24:
Here's a Fusion 360 animation of what I have in mind for the reducer doors.

It's still minimal and very crude but I think it's enough to give you the general idea.

If you look at my version of the board, you'll a series of holes along the outside edge (edge away from the hive). The hinge mounting posts fit into those holes. The servos will be mounted to a case that will cover the board. Bell cranks on the servos will push/pull connecting rods which will operate the arms on top of the doors. The door motion is shown in the animation.

http://www.delong.com/Bee%20Counter%20V3.mp4

hydronics2, 2020-05-25:
wowa... that's really neat. very elegant design.

le0pa-RD, 2020-12-08:
> I agree load cells are super important for looking at hive health and activity.

Hello there, I actually made a weight, temperature, and humidity sensors system to monitor hives, it uses an esp8266 to send data to a central raspberry pi over wifi.
Looking forward to implementing a bee counting system to complete my project.
My only doubt is that IR sensors could get propolized and stop working after a while, has it happened to anyone?

hydronics2, 2020-12-08:
From my experience they actually don't propolize over the sensors... they
do propolize around the sides of the sensors, around the leads, on any
voids or holes.

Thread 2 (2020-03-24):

### ISSUE TITLE
Mouser does not stock TI CD74HC165EE4 part recommended

### ISSUE THREAD

**Issue by owendelong** [hydronics2/2019-easy-bee-counter#2]
Minimum order 1375, multiples of 25, lead time 6 weeks.

It looks like the current best replacement is probably the SN74HC165N ($0.48@Digikey, $0.47@Mouser). It appears that the CD prefix represents an older RCA chip (RCA chips were acquired by TI and duplicate parts are being phased out) while SN prefix represents an actual TI Chip.

Alternatively, if you have a need to stick with the RCA part, the CD74HC165E is available for $0.68@ from DigiKey or Mouser.

**Comment by hydronics2** [comment]
Looks good. I'll update the parts list with the mouser part number [SN74HC165](https://www.mouser.com/ProductDetail/595-SN74HC165N) just to make it easier for folks to order most everything from mouser.

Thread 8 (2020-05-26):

hydronics2/2019-easy-bee-counter #8: I have an idea

m3talover, 2020-05-26:
Hi firstly what a smart and awesome idea for to do this project, congratulations. And you must know i have little knowledge of electronics and their components. i use arduino (or something like that) to do very simple project. i have an idea for improve this project. In mycountry we use color marker to find queen in hives. i think if any chance to add RGB sensors on this gates we get chance to count and know queen behaviours. if you can do it, this made give us to very good data to hive healt, swarn knowledge or use something else for use in bee behaviour researchs.

hydronics2, 2020-05-27:
Hello! yes, I'm currently tinkering with color sensors. If the data looks
good and seems interesting I'll post the results.  If we were trying to
watch out for the Queen we would need a color sensor on each gate.... That
would be a lot of color sensors! My initial interest in color sensors was
to look at pollen color. A lot of bee researchers are interested in pollen.

m3talover, 2020-05-28:
It's interesting to look pollen collor, really good idea too. I'm waiting for your updates.

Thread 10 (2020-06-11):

hydronics2/2019-easy-bee-counter #10: Translate into micropython

jhn4, 2020-06-11:
Hello, i tried to translate your code into micropython, i'm not a vey experienced coder, I dont get it to work really. I'm using the Fipy micro controller from pycom, i don't know if you are familiar with it?
This is the code that i almost copied from your arduino code, it's the same expect how things are written in micropython.
The issue i got is that i don't get anything from the sensors, they're always 0. That makes me think that the issue is in the serial connection.

```
from machine import Pin
import utime
# How many shift register chips are daisy-chained.
NUMBER_OF_SHIFT_CHIPS = 3

# Width of data (how many ext lines)
DATA_WIDTH = NUMBER_OF_SHIFT_CHIPS * 8

# Width of pulse to trigger the shift register to read and latch.
PULSE_WIDTH_USEC = 5

# Optional delay between shift register reads.
POLL_DELAY_MSEC = 1

pinValues = 0
oldPinValues = 0

def read_shift_regs():
    bitVal = 0
    bytesVal = 0
    ploadPin.value(0)
    utime.sleep_us(PULSE_WIDTH_USEC)
    ploadPin.value(1)

    for i in range(DATA_WIDTH):

        bitVal = dataPin.value()
        # Set the corresponding bit in bytesVal.
        print(i,bitVal,bytesVal)
        bytesVal |= (bitVal << ((DATA_WIDTH-1) - i))
        clockPin.value(1)
        utime.sleep_us(PULSE_WIDTH_USEC)
        clockPin.value(0)
    return bytesVal

def display_pin_values():
    print("Pin states: ")
    for i in range(DATA_WIDTH):
        if(pinValues >> i & 1):
            print(" Pin-" ,i ,": HIGH")
        else:
            print(" Pin-" ,i ,": LOW")
    print("\r\n")

#Set up
ploadPin = Pin('P2', mode=Pin.OUT) #Blue
clockPin = Pin('P14', mode=Pin.OUT) #Purple
dataPin = Pin('P4', mode=Pin.IN) #Yellow

clockPin.value(0)
ploadPin.value(1)
pinValues = read_shift_regs()
display_pin_values()
oldPinValues = pinValues
while True:
    pinValues = read_shift_regs()
    if(pinValues != oldPinValues):
        print("Pin value change detected*\r\n")
        print(pinValues)
        display_pin_values()
        oldPinValues = pinValues
    utime.sleep_ms(POLL_DELAY_MSEC)

```

hydronics2, 2020-06-11:
did you start with the example code... test_shift_registers?
https://github.com/hydronics2/2019-easy-bee-counter/blob/master/arduino/test_shift_registers/test_shift_registers.ino

yeah... it looks like Adafruit wrote a little library for the shift out
register 74hc595... It might be helpful to start from this code... buy yeah
writing your own library as a beginner programmer can be a bit daunting!
Maybe post to the arduino forum and see if anyone wants to give you some
pointers? There are lots of helpful people there...

Try posting your question here:
https://forums.adafruit.com/viewforum.php?f=60
If you copy me on your post/answer I'll try to help out too.

hydronics2, 2020-06-11:
here's a link to the 74hc595 library (shift-out) shift register..
https://github.com/adafruit/Adafruit_CircuitPython_74HC595
We need a library for the 74hc165 (shift-in) shift register

jhn4, 2020-06-11:
My code accualy works! The issue was the pload pin was constant 3.3V, so when i switched pins it worked fine!

hydronics2, 2020-07-20:
That's great! Do you have a link to your code?

jhn4, 2020-07-21:
Here is the code, you can post it on your github! I'm not so familiar with Git and you also have the other code so it's better for other people to have all code in the same place!

This code runs on a pycom device, but i think the code will work on any micropython device since the imports are not pycom specific.

from machine import Pin
import utime
# How many shift register chips are daisy-chained.
NUMBER_OF_SHIFT_CHIPS = 3

# Width of data (how many ext lines)
DATA_WIDTH = NUMBER_OF_SHIFT_CHIPS * 8

# Width of pulse to trigger the shift register to read and latch.
PULSE_WIDTH_USEC = 5

# Optional delay between shift register reads.
POLL_DELAY_MSEC = 1

pinValues = 0
oldPinValues = 0

def display_pin_values():
    print("Pin states: ")
    for i in range(24):
        if(pinValues >> i & 1):
            print(" Pin-" , i , ": HIGH")
        else:
            print(" Pin-" , i , ": LOW")
    print("\r\n")

def read_shift_regs():
    bitVal = 0
    bytesVal = 0
    ploadPin.value(0)
    utime.sleep_us(PULSE_WIDTH_USEC)
    ploadPin.value(1)

    for i in range(DATA_WIDTH):

        bitVal = dataPin.value()
        # Set the corresponding bit in bytesVal.
        bytesVal |= (bitVal << ((DATA_WIDTH-1) - i))
        clockPin.value(1)
        utime.sleep_us(PULSE_WIDTH_USEC)
        clockPin.value(0)
    return bytesVal

#Set up
ploadPin = Pin('P23', mode=Pin.OUT) #Blue
dataPin = Pin('P22', mode=Pin.IN) #Yellow
clockPin = Pin('P21', mode=Pin.OUT) #PARPEL

clockPin.value(0)
ploadPin.value(1)

clockPin.value(0)
ploadPin.value(1)

pinValues = read_shift_regs()
display_pin_values()
oldPinValues = pinValues

while True:
    pinValues = read_shift_regs()
    utime.sleep_ms(POLL_DELAY_MSEC)
    pinValues = read_shift_regs()
    utime.sleep_ms(POLL_DELAY_MSEC)
    if(pinValues != oldPinValues):
        pinValues = read_shift_regs()
        if(pinValues != oldPinValues):
            print("Pin value change detected*\r\n")
            display_pin_values()
            oldPinValues = pinValues
        utime.sleep_ms(POLL_DELAY_MSEC)

// Johan

hydronics2, 2020-07-21:
awesome.. updated the code snipit

hydronics2, 2020-07-21:
https://github.com/hydronics2/2019-easy-bee-counter/blob/master/arduino/python.py

closed 2020-07-21 by hydronics2

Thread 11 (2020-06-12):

hydronics2/2019-easy-bee-counter #11: Question

andrijevicnebojsa, 2020-06-12:
Dear Mr. Hudson,
Thank you for this very helpfull project, i ordered everything for both of your bee counters. I have finished this one first and i need to ask you few simple questions. Thank you in advance for answers.
I use adafruit ESP32 and i had to change serial begin to 9600
I. Can i attach sim modul on this esp32 and send data on cloud couse i dont have wireless conection near. 
II. I am getting this results, is this ok or am i missing something

[image]

[image]
[image]
[image]

hydronics2, 2020-06-13:
that looks really good soldering. You can short these pins to get better 'throw' for your IR LEDs.
[image]

hydronics2, 2020-06-13:
As far as the data... the 12 OT 435 means the out sensor at gate 12 was triggered for 435ms. The 12 IT 510 means the IN sensor at gate 12 was triggered for 510 ms. Based on these times and the closness of the triggers the bee counter counted 1 bee coming IN.  later down the serial data shows T 3 1 which means total OUT bees is 3 and total IN bees is 1. (started at the 'out' sensor and ended at the 'in' sensor means the bee was moving IN.... count 1! [image]

andrijevicnebojsa, 2020-06-14:
First I will try sensors in the "field" for a few days without shorting pins, to see results. I will mount it on hive. I will see results and i will give you feedback. But i dont have wifi in the field so for data collecting i must use sim module, but i dont have experiance with connecting sim modul on adafruit.
I am using code that you provide for testing.

hydronics2, 2020-06-14:
how far away is your network?  I've only done a little work with sim
loggers. They are pretty easy, you can just send packets (bee totals) to
the sim logger over serial.

This is a very simple board that logs data locally to an SD card:
https://www.sparkfun.com/products/13712

andrijevicnebojsa, 2020-06-15:
It is very far so i wil try to figure out to connect it with sim module. I have allready made arduino weather station too, and will collect data near hive (humidity (in, out), temp (in, out), UV, wind, rain. I will assemble all this within a few days just to finish code ( i dont have much experiance in arduino codeing), and i will be free to get back to you with some more questions :).

closed 2020-07-20 by hydronics2

andrijevicnebojsa, 2020-07-26:
Hi, sorry for late reply, this is an update. I made some improvements on hive and a central data collection station. I have made two of your projects, one I have already shown you but the other is not working. On first I used adafruit esp32 (I only had one), for the second I had adafruit feather M0 LoRa and adafruit esp8266. I was not able to set any of them to work and I did everything according to your instructions. For LoRa, I chose adafruit feather M0 on arduino ide but it did not want to load the code, and on esp8266 I soldered the shifts register but did not want to accept the code only half of the photoresistor worked. Can you help me what i am doing wrong.
[image]
[image]
[image]
[image]
[image]

andrijevicnebojsa, 2020-07-26:
Can you provide me the code for adafruit LoRa and ESP8266. 
Thank you in advance. This is how hive is looking, i will send you pictures after it is all conected, but just to know it took me a while to finish this up. I am exited and very nervous to get start measuring
[image]

hydronics2, 2020-08-01:
hey there. Sorry for the delay. Did you get the V0 board? or the V1 board?

For the V0 board... you can make it work with the LoRa... if you swap out the shift register chips. Check this out and see if it makes sense. https://github.com/hydronics2/2019-easy-bee-counter/tree/master/instructions/archive

andrijevicnebojsa, 2020-08-02:
I have V1 board.

andrijevicnebojsa, 2020-08-20:
Hi Tomas, i find a solution, i bought another adafruit esp32 feather :).
But now i have one problem when i test gates with paper stick, it shows me  in and out even if i only put papir in. Most of time it detects it like out??
[image]
Did i do something wrong?
Thank you for answer.

andrijevicnebojsa, 2020-08-20:
I also have a problem with Honey bee counter II, I can't make it work. If you allow I will ask a question here.
I can't detect the inputs and outputs with the code you set or I'm not doing something right
[image]
[image]
[image]
Do i have to soldier photoresistor B on gate1 with V2?

andrijevicnebojsa, 2020-08-20:
Do i have to soldier photoresistor B on gate1 with V2?
I have two types of gates but for now none is working, can we make it work

hydronics2, 2020-08-24:
ok... for the EasyBeeCounter... that looks really good. If the shift register code is working.. as you show.. then all the hardware is good.  Looking at the data again... I think it looks good. The information shown is for debugging... so even though it shows information about both gates.. it is not actually counting both gates... 
[image]
Here is what the data is showing...
Gate 6:
Bee is present on the IN sensor for 405ms
Bee is present on the OUT sensor for 420ms
Because the bee was at the IN sensor first and then the OUT sensor... the bee is recorded as leaving the gate. OUT +1
Gate 11:
Bee is present on the OUT sensor for 240ms
Bee is present on the IN sensor for 240ms
Because the bee is present on the OUT sensor first and then the IN sensor... the bee is recorded as moving in through the gate. IN +1
Gate 14:
Bee is present on the OUT sensor for 375ms.
Bee is present on the IN sensor for 390ms.
Because the bee is present on the OUT sensor first and then the IN sensor... the bee is recorded as moving in through the gate. IN +1

Total count for that period is... T,1,2
Bees OUT: 1
Bees IN: 2

hydronics2, 2020-08-24:
I'm sorry I insinuated the data was incorrect at first... now it looks correct.  There are also some other tests... like the time between tripping the in and out sensors has to be reasonable... < 200ms
Also the speed of the bee moving through the gates has to be reasonable... ~<600ms
(I just saw an error in the code where it looks like I use a threshold of 600ms on going IN and 650ms on going OUT.)

andrijevicnebojsa, 2020-08-25:
Do you have maybe solution for Honey bee counter II?
Do you have code for counting?

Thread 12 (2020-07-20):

hydronics2/2019-easy-bee-counter #12: Build Question - 9 pin 22R SIP resistor

kyemacdonald, 2020-07-20:
Hi Thomas,

I am building my first one of these and I couldn't obtain the 10pin 22R SIP resistors locally so ended up with the 9 pin options you have in your alternate parts list.  

Before I solder, could you confirm which pin hole remains unconnected?

Thanks

hydronics2, 2020-07-20:
sure, you need to have the common pin connected... The common pin are
marked with a square on the PCB and also indicated on the SIP with writing
per the cut sheet.

[image: image.png]

hydronics2, 2020-07-20:
[image]

kyemacdonald, 2020-07-21:
Thanks Thomas,

I assumed that was the case but wanted to confirm before I soldered everything up.  It has taken that long for the parts to arrive I didn't want to wreck it!

hydronics2, 2020-07-21:
no sweat. good luck!

closed 2020-07-21 by hydronics2

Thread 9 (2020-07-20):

### ISSUE TITLE
Build Question

### ISSUE THREAD

**Issue by jhaltd** [hydronics2/2019-easy-bee-counter#9]
Quick question about putting this together.  The instructions say, "Install the headers that connect the top PCB to the bottom PCB."  And the accompanying picture shows the headers mounted to the bottom PCB.  How am I attaching the top PCB to the headers on the bottom PCB?  Thanks,

Dunc

**Comment by hydronics2** [comment]
The way I did mine... Is I installed the male headers to the top board and
female headers to the bottom board.
Here's a pictures:
[image: image.png]
In both cases you have to trip some of the pins (only two solder points
provided)

**Comment by hydronics2** [comment]
https://photos.app.goo.gl/SoSMsMpFUZbVFLJF9

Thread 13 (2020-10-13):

hydronics2/2019-easy-bee-counter #13: 2019-easy-bee-counter modify with SD and SIM800 bug

rodece, 2020-10-13:
Hi,

very good job!!!!

I am a italian beekeeper technician, and also an electronic one….,  I collaborate with an association of beekeepers, I have realized your beautiful project to monitor the depopulation of hives due to the use of insecticidal products on crops.
As per your project, I used the Feather M0 with SD card as there is no wifi signal for data transfer in the stations in my areas.
I modified the sketch with the data saving function on SD and it works fine, now I wish I could use the data transfer on the thingspeak site using the SIM800L card (I did the tests with Arduino and a DTH22 sensor and it works fine).
I connected the SIM800L on the Rx Tx port of the Feather by activating the serial1,
I then modified the sketch, created by you, to use the SIM800 and when compiling it does not report any errors, the AT commands do not give any errors but the bee count does not work it seems that it is blocked by the sim800 protocol. Commenting on lines 706 to 775 the counter works but clearly not the SIM800L.
Some idea ??
Thank you

[bee_counting_0907_davide_ok_rtcM0_sim800_ver5.zip](https://github.com/hydronics2/2019-easy-bee-counter/files/5370193/bee_counting_0907_davide_ok_rtcM0_sim800_ver5.zip)

hydronics2, 2020-10-13:
hmmmm... do you think it is related to writing to Serial1? try writing to Serial1 in setup and see if that works. Serial1 pins are free and should work.

As an aside, did the SD card work? The MISO, SCK lines are tied up writing to the shift registers. Apparently the shift registers I choose (the ones everyone uses) are not true SPI devices and don't work as expected when you pull the chip select HIGH... So you can't share the SPI with another device (like the SD card)... but maybe it worked for you? [Here's a little more information about this issue... ](https://electronics.stackexchange.com/questions/121249/how-to-put-a-74hc165-on-an-spi-bus)

I would initialize the SIM800L module in setup if possible... Make sure you're not blocking the code and the delay statements are not 'hard delays', that is, write to the module at intervals in line 625, make sense?

`if (millis() -  previousMills > intervallo ) {
Serial1.println("AT");
  delay(1000);

  Serial1.println("AT+CPIN?");
  delay(1000);
....................................
`

rodece, 2020-10-21:
Hi

,
I managed to get it to work partially (but for now it can also be fine ...).
I fixed the sketch by creating different voids, one for the serial, one for the SD and one for the SIM800, then inserting them on the loop from line 568 with common execution time control, currently 2 minutes.
Now it does not count for only 45 seconds during the writing to SD and the subsequent activation of the SIM800 to download data on the site.
More than good !!!!
They advised me to create an array for the section on sending AT commands to the SIM800  ( 705 - 778 )in order to eliminate a good part of the delays.
I'm working on it, even if I have some difficulties ... ...
[bee_counting_1410_ok_SD_sim800_ver5.zip](https://github.com/hydronics2/2019-easy-bee-counter/files/5418470/bee_counting_1410_ok_SD_sim800_ver5.zip)

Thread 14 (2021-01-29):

hydronics2/2019-easy-bee-counter #14: Share HSPI with lora RFM95 module

Christophe45, 2021-01-29:
First many for your project!! it's working very well, I like it. 
Since 1 week I face to an issue, I want to had your bee counter to my system. 
I developed a PCB with an ESP32 wroom 32 with weight sensor, temperature, GPS, an accelerometer and everything uses the LORA system. My Lora module is an RFM95 which uses SPI (VSPI). I tried several things in order to share the VSPI bus as a slave but it doesn't work. I tried using the HSPI bus for your count. Only everything works well but when I put the Lora system nothing works ... Do you have an idea to make everything work? I can share everything with you :)
https://github.com/Christophe45/ESP32-Lorawan
Many thanks in advance for your help :)

hydronics2, 2021-01-29:
Did you see this?
https://github.com/hydronics2/2019-easy-bee-counter/tree/master/instructions/archive

" I made a few mistakes on the first version (v0). The 74hc165 is not a
true SPI device. It doesn't have a tri-state buffer on the MISO...."

Christophe45, 2021-01-29:
Many many thanks Thomas for your answer, I will try this :).

have a nice week-end 

christophe

https://github.com/hydronics2/2019-easy-bee-counter/tree/master/instructions/archive

Christophe45, 2021-01-30:
Hi Thomas,

Now I undersand more, but if I use the 74HC589 I need the re-make a new PCB as the Pins are differents with the 74HC165... :(

If I have to re-make a PCB, I will may be try to use register that using I2C :)

A a nice day

christophe

Le vendredi 29 janvier 2021 à 19:31:31 UTC+1, Blain Christophe <blain.christophe@yahoo.fr> a écrit : 

Many many thanks Thomas for your answer, I will try this :).

have a nice week-end 

christophe

https://github.com/hydronics2/2019-easy-bee-counter/tree/master/instructions/archive

hydronics2, 2021-01-30:
If you are using the PCB v1 then I already made the changes and you can just swap out the shift registers and it will work.
[image]

Christophe45, 2021-02-01:
I have the same PVB V1 my question was link to the register 74HC589 that you  discribe here:

 In order to work with the LORa module you need to swap out the 74hc165 shift registers with true SPI based shift registers... like the 74HC589 referenced in the above stack exchange answer.

The pinout of the 74HC165 is diffent of the 74HC589 so you can't install at the same place?

Many thanks in adanve for your answer :)

Christophe

hydronics2, 2021-02-01:
damn... that right.... the HC595 has a different pinout!... so that's not an easy solution... that's too bad. 

I should have probably designed a tri-state buffer into the design like Paul S. suggests here: 
[image]

https://www.pjrc.com/better-spi-bus-design-in-3-steps/

tri-state buffer: [74AHC1G125](https://www.digikey.com/en/products/detail/diodes-incorporated/74AHC1G125SE-7/2639244)

I've used one of these in a circuit once. Unfortunately there's no through-hole version. You could try to patch one of these in with some small wires and hot glue. It's totally doable but a bit tricky to solder! You'd basically cut the trace on the MISO line and add jumper wires between the pins... and add an enable jumper wire to the OE pin.  

[image]

Per the data sheet, pulling the OE pin high would free up the MISO line for other uses. What do you think?

Christophe45, 2021-02-02:
Many thanks Thomas for your answer :), I will look that ;). But before I will try Bit-banged SPI : https://www.gammon.com.au/forum/?id=11979&fbclid=IwAR0evnHg7Bk4rl7QrX_K8_500TE5-9ZDSsS4beKH7vyye8QyhOgowQofdF8

In order to try with others Pin the SPI :).

I will let's you know :)

christophe 

https://www.pjrc.com/better-spi-bus-design-in-3-steps/

Christophe45, 2021-02-04:
I succeeded with the  Bit-Banged SPI with your sytem and using normal SPI for my LORA RFM95 module :)

Now I will try to make and other PCV with my system ( Weight, temp, GSP, accelerometer and light sensor) :). If you want I can share you my system a this end :)

Best regard,

christophe

Le mardi 2 février 2021 à 08:32:36 UTC+1, Blain Christophe <blain.christophe@yahoo.fr> a écrit : 

Many thanks Thomas for your answer :), I will look that ;). But before I will try Bit-banged SPI : https://www.gammon.com.au/forum/?id=11979&fbclid=IwAR0evnHg7Bk4rl7QrX_K8_500TE5-9ZDSsS4beKH7vyye8QyhOgowQofdF8

In order to try with others Pin the SPI :).

I will let's you know :)

christophe 

https://www.pjrc.com/better-spi-bus-design-in-3-steps/

hydronics2, 2021-02-04:
Great, bit-banging was a good idea.

chinswain, 2024-06-01:
Hi @Christophe45 , do you have a build log of your system? It sounds very interesting - what are you using the accelerometer for?

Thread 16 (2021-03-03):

hydronics2/2019-easy-bee-counter #16: all ir are blinking except gate8

padrian2s, 2021-03-03:
I love this project and I'm trying for the second try to make it works. In the blink test all ir are blinking except gate 8.
On the shift registers test only gate 3 is working and is triggering all the gates together.
Any sugestions on how to check what's going on in the code or on the board?

thanks!

hydronics2, 2021-03-04:
Ok, sounds like you are making good progress. I would check that you have solder on all the pins.  Each gate's LEDs are in series.... if you miss a solder joint, it will show up as the entire gate (both LEDs) not getting power.

hmmm as far as the shift registers... seems like something is definitely throwing everything off. I feel I've ran into this issue before but I cant recall.

padrian2s, 2021-03-04:
Hi Thomas,

Thank you for quick response. I will re-check the soldering part on that gate. I'm using "Adafruit Itsy Bitsy 32u4 - 5V 16MHz"
but also I ordered the Feather ESP32 so I'm trying to get the identical and reduce the root cause of problems.
I'm very curious since I checked the entire board with multimeter:

- input voltage on every pin, leds and shift registers.... all good.
- I also ring some of the circuit paths

My initial tought was that since I'm using different microcontroller maybe shifts registers are not compatibile with SPI but how and why only gate 3 is detect motion and only gate 8 is not working in the IR test.

My PCB was printed in December 2020 at jlcpcb so the missmatch in design is highly improbable. I looked over the code but I can't find anything. 
If you have paid support I will gladly accept this to help me out.

Again, this project is really cool and I appreciate your work and future ideas

padrian2s, 2021-03-05:
Hi Thomas,

Is working! I replace the itsybity with Feather ESP32 and is working just fine!! I can't belive it, by first opensource hardware project is working.

Thank you!!!

closed 2021-03-05 by padrian2s

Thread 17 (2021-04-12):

hydronics2/2019-easy-bee-counter #17: Bee counter that is based on state transition instead of elapsed time

svavassori, 2021-04-12:
First of all I'd like to thank you to put freely available the design of the board and the code to run it.

Looking at the Arduino code I saw that your counter is based on time threshold (200 ms and 600-650 ms) to avoid some bouncing in the reading.

This gave me the idea to try to detect the entering or the exiting pattern in a way that is robust with respect to the bouncing of a **single** sensor of the gate at a time. This gist ( https://gist.github.com/svavassori/431e78c2d9f1ff55adb63623408eb033 ) implements a state machine that detects the entering or exiting of a bee for a gate, the extension to multiple gate can be easily done be extending the `State current[]` array to the side desired.

Unfortunately I have no access to a beehive until some months, so I was wondering about these two possibilities:

* if you could test it on your board (the integration shouldn't be difficult) to see if it actually works, or
* if you could share some unfiltered captures of a single-gate sensors (in-out) in order to have real sequences, so I can test it by myself and see if it works.

Regards,
SV

hydronics2, 2021-04-13:
Hey, I don't have an active hive right now either...

That's a great idea of sharing unfiltered data. I did capture some on
another laptop for just that purpose. I'll see if I can dig it up.

svavassori, 2021-04-17:
If you could find those, it would be awesome because it will also validate (or invalidate) the assumption of a single sensor change per gate.

Let's hope for the best!

svavassori, 2021-05-19:
Do you have any news about the raw capture of the gate?

rodece, 2021-06-23:
> Do you have any news about the raw capture of the gate?

Hi,

I am interested in the variant of the project, I have the system available on a hive from which I detect the data as a protocol created by hydronics2 ( very beautifull), you can check  the data is as follows link :
https://thingspeak.com/channels/1141102
as you can see I have some problems as the data between bees in and bees out are not very aligned, some days the variant is also 15000 bees,
I think the problem is on the setting of the times, I made several changes without solving the problem.
if you have the possibility to send the sketch already compiled on the arduino system, not in C,  I will install it for testing.

svavassori, 2021-06-24:
@rodece I saw you have almost 20k bees as difference between out and in count over a 24h period, that's really strange. Usually **out count** should be a little higher than **in** because bees are dying outside and are born inside, so you have a net flux from inside to outside, but what you got is way too big for a single day.

Moreover it seems that the temperature sensor could be exposed to direct sunlight since it peaks at 11:00 instead of at 16:00-17:00

I don't have an Arduino here because I'm using an ESP32, but before plugging in the state machine, I would like to ask if you can run this sketch to get some raw data: https://gist.github.com/svavassori/37b6db89e4ab47f45748939dbb8f16b2

It's a stripped down version of @hydronics2 one that prints to the serial line only the raw values of sensors at Gate 0 for each loop. In this way we can see how much debouncing (spurious state transition of the sensor) there are and if the precondition on which my solution is built is met (singe sensor transition at a time). If that condition isn't met, the current implementation will go in an error state and so wouldn't be of any use.

The idea is to record what it is read from the sensor (a dozen of bees entering and exiting should be enough) in order to understand the timings and the cases that we face and then to find a solution to properly count the bees (or at least reduce the false counts to a number so small that it doesn't impact on the final result.
Please, pay attention that this version doesn't count, it simply prints the state of each sensor, so it is important also to observe the gate and count them manually (or record a short video) in order to know what was actually happening.

Since gate 0 is the first one, probably it won't be so frequently used by the bees, so closing some other gates with a stick of wood for a couple of minutes can help in getting the results in a shorter time. :-)

rodece, 2021-06-27:
@svavassori 
> I saw you have almost 20k bees as difference between out and in count over a 24h period, that's really strange. Usually **out count** should be a little higher than **in** because bees are dying [...]

Yes, you are right, however in these days there was a high import, today the values   are more correct.

> Moreover it seems that the temperature sensor could be exposed to direct sunlight since it peaks at 11:00 instead of at 16:00-17:00

The sensor is installed behind the hive, but the apiary is installed in a wood and the sun only comes around 12 o'clock

I have two bee counters with feather M0, on the second I made the modification you requested and the data can be found in:
https://github.com/rodece58/contavoli 
 as you can see they make mistakes, I think due to the fact that the bees can also transit by walking on the sides of the gate and perhaps they are unable to engage the two sensors. 
I think try to tighten the gates and do the test again , I just have to check if the drones pass.

svavassori, 2021-06-28:
@rodece, thanks for your files, they have been very helpful to do an offline analysis.

As first I tried to run the state-machine as it is but it got stuck too many times to be happy with, so I changed its behavior to reset itself when the gate comes empty again: in this way it doesn't block and just skip the problematic parts. Unfortunately, by doing some stats, it came out that it counted:

* 53 incoming bees
* 3 outgoing bees
* 23 error sequences

This means a 41% of sequences aren't handled properly, and that is not a good number, so probably my assumption of a single-change isn't that right.

Then, I calculate the time it took for each detected bee to pass through the gate, in order to have an idea of the time it needs and the results are interesting, I plotted them in this simple frequency chart:

[image]

As it can be seen, filtering below 650 ms it would cut out more than 20% of the counted bees (13 over 56), so at least the idea of being time-independent does make sense, because of the variance of the distribution.

Another interesting thing of the raw data is that it can be seen there are some bees on the inside that check the gate (starts from the inside but then go back) while the bees that are coming in are pretty resolved and traverse the gate without too many doubts.

About tightening the gate, in order to let the drone pass you could tighten just the first and leave some others open. Of course this will imply we aren't counting all the bees, but just to test if it reduces the errors it could be enough.

I saw you uploaded the videos (thanks a lot!), I'll take a closer look later on, but at least they validate that it was mainly an incoming traffic. At first sight, in one of them it seems there are two bees entering at the same time, would that be possible or it's just the point of view of the camera?

svavassori, 2021-06-29:
I had a look at the size of the gate on the PCB schema and compared with other references: I think the gate is definitely too big and  bees could probably pass on the sides without being detected by the sensors.

From the schema, the gate should be 9.85x15.3x8.4 mm (WxLxH) while the two sensors are around 2 mm wide, this means there is 4 mm on each side that can be used by the bee. Could you please check those measure (9.85x8.4) matches the build one?

[image]

Looking at [this](https://raw.githubusercontent.com/hydronics2/2019-easy-bee-counter/master/pics/finished2.jpg) image, it can be seen how much space there is.

As reference, the classical metallic entrance has gates of 7.8x7 mm (WxH) and the grid of the queen excluder is spaced 4.1 mm, so if the above measures are correct, it means the gate should be shrunk by 1.1 mm on each side; some black tape should be enough for testing.

It could be that also the bottom would benefit of a lift of 0.5-1 mm, in order to avoid two bees passing on top-bottom, but first I would prefer to see how the counter behaves only with shrinking.

rodece, 2021-06-30:
@svavassori
Good job !!!
I confirm that the bees also walk on the sides of the gate, see video 4.
I checked the port measurements and they are 97L x 87H under the sensor. I changed the dimensions of the doors with black plastic sheets, now they are 80L x 70H under sensor. I did the test on 3 hives with different traffic, the data have improved even if not completely.
https://github.com/rodece58/contavoli/tree/main/log_30_06
On Saturday I try on the same hive as the first tests and load the log.

svavassori, 2021-07-01:
In `log_arnia_1.txt` there aren't any inconsistent sequences, so it seems it is mostly working, however in the video I see 7 bees entering; it is possible that there is a time misalignment between the video and the raw data.

In `video_arnia_3_new.mp4` there are too many bees to be able to count, and the increased wrong sequences is probably due to the fact that they are entering one behind the other. Another confirmation of that is in `video_arnia_5_new.mp4` there are less errors and it is less crowded. This is a limitation of the system that I don't think is possible to resolve since we cannot ask bees to enter one-by-one with some space. :-) At the same time, I can imagine that with all the gates working, it wouldn't be that crowded.
Are they doing some _washboarding_ on the top surface?

In `video_arnia_5_new.mp4` it seems that sometimes two bees are trying to enter and when they reach the sensor only one of them passes. A small improvement would be to level with some strips the top part so the sensors don't extend from the surface, this will also reflect the 7 mm high right from the entrance.

When you will do your next Saturday test, I would also ask if you can change in the Arduino code the last `delay(15)` to `delay(9)` in order to increase a little the sampling frequency from 62 Hz up to 100 Hz. I don't expect any major benefits but it is just to see if it can help in differentiate some edge cases.
From the specs we have to do a minimum LED off time of 7.5 ms, so we have still some margin.

rodece, 2021-07-05:
I make a  tests, find the results on
https://github.com/rodece58/contavoli/tree/main/log_03_07,
 I changed the delay as per your instructions.
I have also modified the gate by inserting an internal 8mm tube, see attached photo, now only one bee passes !!! ;-) 
The data seems to have improved.
As you said there is too much traffic on a gate, to reduce the errors perhaps it would be better to be able to enable an another 3 - 4 gates to check if the counter is working correctly.

svavassori, 2021-07-05:
> I have also modified the gate by inserting an internal 8mm tube, see attached photo, now only one bee passes !!! ;-)

I saw from the videos that with the tube it seems they slips and it is problematic for them to enter upside down.

> As you said there is too much traffic on a gate, to reduce the errors perhaps it would be better to be able to enable an another 3 - 4 gates to check if the counter is working correctly.

Sure, with less traffic should perform much better.
The mention I did about closing _some_ gates was to increase, if needed, the traffic through the monitored gate, not to let _only_ that open :-)

Thanks for the new dataset, here is the relative frequency chart:

[image]

This confirms two things:

1. bee traversal can have a big variance
2. there are false positive

A gate traversal in 50 ms is very unlikely to be a real bee (walking 20cm/s is too fast), so anything below 100 ms would be suspicious, and probably is due to two bees at each side of the gate that accidentally trigger a sequence that matches an inbound (but it could be an outbound as well). Nonetheless this is not a big problem since it can be easily filtered by doing some stats and see what is a reasonable minimum time to get through the gate.
A possible way to have some reasonable value about that threshold is use piece of transparent tube as gate and record a video on top of it with a millimeter band next or under. The visual assessment of the speed has to be done manually but it is a one-off.

On the other hand, that false positive made me think about the impossibility to guarantee a _false positive free_ counter with a two sensor gate: two bees could just stay there for the right amount of time to be in the "likely" range and there will be no way to distinguish it from a real arrival or departure. It shouldn't be impact a lot on the big numbers because I suppose it would average to zero between false arrivals and false departures and it will mostly happen when there is "traffic jam", but it is an intrinsic limit of this solution.

That led me think about using 3 or 4 sensors (inline) per gate: it should resolve this problem and probably, by using 4, it will also be able to differentiate:

1. two bees trying to pass and which one wins
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

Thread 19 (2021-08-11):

hydronics2/2019-easy-bee-counter #19: False triggers because of sunlight

kim-ado, 2021-08-11:
I would like to first of all thank you for making this project, it is a brilliant idea!

I recently built this project, and works like a charm inside where there is no sunlight. However, when outside the sensors are all over the place with false triggers constantly. How to mitigate this issue?

hydronics2, 2021-08-11:
I think I've seen that issue when the sun is in low angle positions. So say early morning and the sun is shining into the gates such as,, early morning hive is facing East or late afternoon when hive is facing West. Does that seem to fit your situation? Maybe putting a small planter ~1ft in front of the hive?

kim-ado, 2021-08-11:
Hi and thanks for quick the answer!

The sensors seems to be constantly triggered in the middle of the day (recently tested at 14-16 pm) here in Trondheim Norway. Putting the counter in the shadows seems to mitigate this issue, but it will still be unstable. I've thought about 3D printing a cover of sort with extended roof and/or removing the soldering from the jumpers to decrease throw range of the IR sensors. Any other tips or tricks are greatly appreciated!

hydronics2, 2021-08-13:
I take it the bottom PCB is black, right?... Maybe the sheen on the PCB is reflecting the IR. Maybe try putting some black tape in the gates to better absorb reflecting IR?

kim-ado, 2021-08-24:
It seemed like the landing plate for the bees was reflecting sunlight, putting some black tape on that proved to work! Thanks for the suggestion.

closed 2021-08-24 by kim-ado

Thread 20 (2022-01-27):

hydronics2/2019-easy-bee-counter #20: Suggestion: Make a shorter version with 12 gates instead of 24

oskarscholander, 2022-01-27:
I love this project!

I would suggest adding a short version that supports 12 gates instead of your original 24. Some type of hives here in Sweden doesn't have as wide opening as Langsroth has.

chinswain, 2022-03-20:
+1 for the UK also, 90% of beehives here are National with small entrances (5").

chinswain, 2022-04-16:
Hi all, my PCBs arrived today:

[image]

I'm trying to work out a way to mount it to my hive as it's a little long. Would anyone be able to shorten the PCB design to 34cm or less?

[image]
[image]

oskarscholander, 2022-04-19:
This would be a great improvement to this project. In your case you are quite easily able to cut away some of the box material, but the most common hive entries in Sweden are

oskarscholander, 2022-04-19:
This would be a great improvement to this project. In your case you are quite easily able to cut away some of the box material, but the most common hive entries in Sweden are only 12cm long.

I would love to have the knowledge on how to change the schematic properly but I don't know how :D

chinswain, 2022-04-19:
Unfortunately it is a shared hive, I've been disallowed from cutting it. I'm currently learning Kicad, I think we can modify the design fairly easily.

oskarscholander, 2022-04-19:
Aaah I see.

Haha, I downloaded Kicad right after I wrote the last comment to you! 😂 Let's try to do this!

oskarscholander, 2022-06-07:
@chinswain I wont be able to create a shorter version.

Do u have a spare PCB to sell to a fellow beekeeper in Sweden?

chinswain, 2022-06-08:
I've cut mine and starting building them so no spare.

oskarscholander, 2022-09-21:
@chinswain hope your hives are healthy! How is the bee counter project going?

selmanonal, 2023-02-16:
Is anyone who made shorder version of the pcb?

chinswain, 2024-04-27:
I've started looking at this again.

I cut the PCB as pictured (discarding bottom half) and soldered the components, LED test works:
[image]
[image]

But unfortunately the shift registers do not. I'm not sure why as there are no missing connections that I can see for the 3rd (and now last) 74HC165 caused by the cutting.

Here's the modified shift register test code, I've removed the 4th, 5th and 6th:

```#include <SPI.h>

const int LATCH = A5; 

const byte powerGates1 = 15;

void setup ()
{
  
  SPI.begin();
  SPI.beginTransaction(SPISettings(3000000, MSBFIRST, SPI_MODE2)); //3Mhz
  
  Serial.begin (115200);
  Serial.println ("Begin switch test.");
  pinMode (LATCH, OUTPUT);
  digitalWrite (LATCH, HIGH);

  pinMode (powerGates1, OUTPUT);
  digitalWrite(powerGates1, LOW);
  
}  // end of setup

byte switchBank1;
byte oldSwitchBank1; 
byte switchBank2;
byte oldSwitchBank2; 
byte switchBank3;
byte oldSwitchBank3; 

void loop ()
{
  digitalWrite(powerGates1, HIGH);
  delayMicroseconds(15); //first 24 gates only need 15us while gates closer to the end need ~40us-75us
  
  
  digitalWrite (LATCH, LOW);    // pulse the parallel load latch
  delayMicroseconds(3);
  digitalWrite (LATCH, HIGH);

  delayMicroseconds(3);
  
  digitalWrite(powerGates1, LOW);

  switchBank1 = SPI.transfer (0); //8
  switchBank2 = SPI.transfer (0); //16
  switchBank3 = SPI.transfer (0); //24
  
  byte mask = 1;
  int sensor = 1;

  for (int i = 1; i <= 8; i++)
  {
    if ((switchBank1 & mask) != (oldSwitchBank1 & mask))
      {
      Serial.print ("Switch ");
      Serial.print (sensor);
      Serial.print (" ");
      Serial.println ((switchBank1 & mask) ? "ir triggered" : "none");
      }  // end of bit has changed
    mask <<= 1; 
    sensor++; 
  }  // end of for each bit

  mask = 1;
  sensor = 9;
  for (int i = 1; i <= 8; i++)
  {
    if ((switchBank2 & mask) != (oldSwitchBank2 & mask))
      {
      Serial.print ("Switch ");
      Serial.print (sensor);
      Serial.print (" ");
      Serial.println ((switchBank2 & mask) ? "ir triggered" : "none");
      
      }  // end of bit has changed
    mask <<= 1; 
    sensor++; 
  }  // end of for each bit

  mask = 1;
  sensor = 17;
  for (int i = 1; i <= 8; i++)
  {
    if ((switchBank3 & mask) != (oldSwitchBank3 & mask))
    {
      Serial.print ("Switch ");
      Serial.print (sensor);
      Serial.print (" ");
      Serial.println ((switchBank3 & mask) ? "ir triggered" : "none");
    }  // end of bit has changed
    mask <<= 1;
    sensor++;  
  }  // end of for each bit

  oldSwitchBank1 = switchBank1;
  oldSwitchBank2 = switchBank2;
  oldSwitchBank3 = switchBank3;

  delay (20);   // must be greater than 7.5ms (see notes at top of code)
} ```

chinswain, 2024-04-27:
I just tested using a TV infra red remote control which triggered all of the sensors using the above script so I'm not sure what the issue is, must be the LEDs?

chinswain, 2024-05-01:
The new NDP6020P arrived today, same issue. Does anyone have any ideas?

Bypassing the MOSFET:

[image]

With NDP6020P

[image]

hydronics2, 2024-05-02:
Hey, I'm just trying to catch up... What is the problem? The IR LEDs are not triggering a 3.3V sensor output? Is that correct?

I see you tested the shift registers by shorting 3.3v to the shift register input. That was smart to test. There is also sufficient IR in any semi-direct sun light that will also trigger the sensors and perhaps your IR remote control (I never tried that but cool idea). I like to use a small piece of white paper at a short distance away from the sensor (about 1/4" to 3/8").

Be careful with those LEDs! The LEDs work OK with the 22ohm resistors installed. Good enough to test the functionality of the shift registers. Once the jumpers are soldered, the LEDs should only be allowed to stay ON for 100ms.... otherwise they will burn themselves out.

[image]

chinswain, 2024-05-02:
Hi Thomas,

Thanks for replying and thanks for making the PCB available to the public.

The problem is the LED's are barely lighting up, I cannot work out why. Bypassing the MOSFET pads 2 & 3 proves everything is soldered correctly but using the MOSFET the LED's barely light up at all. From crude testing I  assumed there was an issue with the NDP6020P from china, so ordered a few from Amazon and eBay (It's no longer available from reputable stores).

After many failed attempts at modifying in KiKad we've cut your PCB in half, in theory it should work looking at the schematics. We cut it exactly here:

[image]

Everything works fine, gates respond to an IR remote and IR LED's on cameras trigger them. Any ideas?

hydronics2, 2024-05-02:
Ok, so when you bypass the mosfet (shorting across the mosfet) everything works?  LEDs trigger the sensors?

[image]

FYI, you don't want to bypass the mosfet if you have soldered these jumper pads.... Does that make sense? I'm not sure the documentation emphasized this enough. The LEDs can get damaged if the forward voltage is at 3.3V for any length of time over 100us.
[image]

chinswain, 2024-05-02:
Exactly, via a webcam with the IR filter removed they are very bright, pads are open and when I short the MOSFET pins it's for less than a second.

hydronics2, 2024-05-02:
Ok, if those solder pads are open then you can short the mosfet all day and there is no problem.  

The other mosfet you mentioned, the [NDP6020](https://www.onsemi.com/pdf/datasheet/ndp6020p-d.pdf), is a P-channel mosfet. The one we need is an N-channel mosfet. The generic one I listed the [FQP30N06](https://www.mouser.com/ProductDetail/512-FQP30N06L) is super generic. It should work fine but you can substitute another one as long as it is type N-channel and the threshold voltage is around 2.5V, and the pinout is the same (the ordering of the pins is G, D, S as opposed to D, G, S or something else).  The threshold voltage is the voltage needed to turn it ON.

Try jumping 3.3V to the Gate 'G' pin. This should mimic the way the micro-controller turns the mosfet ON. If that works then you may just have a damaged trace from the micro-controller to the 'G' pin. This is common when you solder/resolder. Its easy to fix by adding a little jumper wire between the micro-controller pin and the 'G' pin. 

[image]

chinswain, 2024-05-02:
jumping 3.3V to the gate produces the same result (very dim LED's). I've checked the traces with a multimeter and can't find any breaks, the 3.3V signal is making it to the gate pin of the MOSFET.

I noticed the drain is only 2v when under load, without the LED's it's 3.3v on a breadboard, if I add a standard LED to the drain and 3V source it drops from 3.3V to 2.6V.

Everything points towards the MOSFET I think? Bizarre as I've tried three some different sources...

ChatGPT suggests [IRF3708PBF ](https://www.mouser.co.uk/ProductDetail/Infineon-Technologies/IRF3708PBF?qs=2r01AXMCG3P2FLBF0Ge6xA%3D%3D)as an alternative, Vgs is 2.8V.

hydronics2, 2024-05-03:
I think both mosfets should work... but sticking with the FQP30N06L for now... 

Can you check the voltage at the Drain pin when the gate is triggered ON. Looking at the FQP30N06L datasheet there should be ~40mV resistance between the drain and the source. If we do our LED math and evaluate the current across 2 LEDs, with forward voltage of 1.25V each, supply voltage of 3.3V, and a 22ohm resistor, our current is about 36ma.

So the voltage drop across the mosfet from drain to source is 36ma x 40mV => 0.001V... so pretty much nothing. Sorry to be rambling on here... I'm just thinking out loud because its been awhile sense I looked at this and to be honest I haven't considered for some time the resistance of an N-channel mosfet. I knew it was small but that is really small. So we should be getting good current passing through this mosfet with little resistance... 

All this is to ask, can you verify again what voltage you are reading at the drain pin when the gate is triggered ON? Could it be you have a short somewhere on your gate pin? Does the gate pin show a resistance of 10k to ground?

[image]

chinswain, 2024-05-04:
Hi Thomas,

It looks like it was the MOSFET, I replaced it with this and it's working perfectly:

IRLB8721PbF
N channel power MOSFET
TO-220 Package
Vds = 30V max
Max current = 62A
Vgs = 2.35V max
Rds_on = as low as 8.7 milliohm - depending on Vgs

https://cdn.shopify.com/s/files/1/0176/3274/files/irlb8721pbf.pdf?v=1646930126

Thanks for replying!

So that confirms it - if people want a shorter version, just cut exactly as shown.

hydronics2, 2024-05-05:
good to hear! I made a note on the readme page

closed 2024-05-05 by hydronics2

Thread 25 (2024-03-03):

hydronics2/2019-easy-bee-counter #25: Bug report: Connection missing for Itsy Bitsy on printed bord

JanolovV, 2024-03-03:
Hi,
I'm working on an Easy Bee Counter and got into trouble in the testing phase, no data from the shift registers. After a long and troublesome (for an amateur like me with limited equipment) I finally found out what is wrong. There is no connection on the printed board between the SCK on my Itsy Bitsy controller and the CLK on the shift registers. So it can't work with any Itsy Bitsy with this design. The clock connection does not go to any other pin on the Itsy Bitsy either.
I checked the corresponding clock connection for the ESP32 controller and there the connection is ok so it's possible to solve the problem with a very short patch.

I'm glad I could figure this out before the bee season starts.

Regards
Jan-Olov

hydronics2, 2024-03-07:
wow that is strange and really unfortunate.  Good job finding it! I tested the board but must have a different gerber file posted. I don't have any PCB tools on my computer right now but I used some online tools....

It looks like the Gerber files do not include the SCK connection for the itsybitsy footprint as you found. You are correct, you can jumper from the ESP32 footprint.

The Eagle schematic shows the SCK pins connected on both footprints on the schematic and board files.
[image]

[image]

It looks like it is missing on the kiCad Schematic and board files. See below missing trace.
[image]

Thanks for finding that. I am going to delete the gerber files and make a note on the kiCad schematic.

JanolovV, 2024-03-08:
It was a bit tricky to troubleshoot. First I suspected the shift registers and desoldered them to test them properly. That was a bit tricky and it would have been a good idea to have them in sockets instead. Now all the shift registers I desoldered was in fact ok but one of my spares was not. So I would strongly recommend using sockets for both the shift registers and for the processor board. It makes troubleshooting so much easier.

I also tested the "photocells" while the shift registers where of the board. A simple program that "blinked" the photocells 3 s on 3 s off which gave me time to check with a multimeter that the signal came through to the right contact on the shift register socket that I welded on and I could use my finger to trigger the detection. I think this might also a better way to test the "photocells" than trying to see the IR light which none of my phones or cameras could.

Kind regards
Jan-Olov

hydronics2, 2024-03-08:
Nice job. Well hopefully now that you have done the work, there'll be less
to troubleshoot for the next person!

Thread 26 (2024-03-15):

hydronics2/2019-easy-bee-counter #26: A comment on the final assembly

JanolovV, 2024-03-15:
After reading earlier discussion about making the passage for the bees narrower I bought lower female headers (Mouser 30483508) about 2 mm lower. After cutting the middle four connectors with a cable cutter I also grinded down the edges with a Dremel. That saved me another mm. I also needed to cut away a small part of the header on the opposite side of the first pull down SIP resistors (and under the screw connectors). One of the resistor legs comes through right where the header is suppose to sit.

Kind regards
Jan-Olov

chinswain, 2024-06-07:
What size is the final gate? Did you reduce the width?
I found some 4.3mm height female headers which would reduce the vertical gate size to 7mm. I think maybe a 3D printed insert to reduce the with to 7mm also would help.

JanolovV, 2024-06-07:
My final gate height is 9 mm and I have not reduced the width. Of course 7 mm is better than 9 but we still have the width 10 mm if you dont do anything there to. 

Having read the problem others have had to reduce errors in the interpretaion of the signals I doubt it is worth the effort. You are likely to still have some errors whatever you do since the design does allow the bees to act randomly. If you had some kind of device that made it impossible for the bees to go back once they entered the gate you would be fine. But I think it's better to accept the design as is and if possible just reducing the gate size a bit to avoid serveral bees at the same time in the gate. If we accept that there will always be errors and that the calculation of bees in and out never will add up correctly. We still get a lot of information about what is going on in our hives. We can see when activity is high and combine it with other measurements like ambient temperature and hive weight to learn more about the little creatures.

Making measurements allways tell you something but not allways what you expect. I measured temperature and humidity in three hives during a winter. I expected it to vary with ambient teperature. They had almost constant temperatures of 10, 15 and 20°C respectively through the whole winter. (I don't remember the humidity but that was also pretty much constant.) The temperature was an effect of how close the sensor was to the globe of bees. So there is very little point in measuring temperature in the hive. The bee thermostat regulates it. If temperature should drop during winter the bees are dead and there is nothing you can do until spring anyway.

Jan-Olov

JanolovV, 2024-06-07:
Thank you for your question!
I commented on Github

Regards
Jan-Olov

<https://www.avast.com/sig-email?utm_medium=email&utm_source=link&utm_campaign=sig-email&utm_content=webmail>
Virusfri.www.avast.com
<https://www.avast.com/sig-email?utm_medium=email&utm_source=link&utm_campaign=sig-email&utm_content=webmail>
<#DAB4FAD8-2DD7-40BB-A1B8-4E2AA1F9FDF2>

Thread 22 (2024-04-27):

### ISSUE TITLE
Using HUZZAH32 onboard LDO for 12 gates?

### ISSUE THREAD

**Issue by chinswain** [hydronics2/2019-easy-bee-counter#22]
The LDO on the HUZZAH32 can peak 500mA, half of this is used for the board itself - Do you think 250mA would be enough to power 12 gates?

Hydronics2 mentioned that 75us and off for ~30ms results in an average power draw of around ~50ma at 5V for 24 gates so seems ok?

**Comment by hydronics2** [comment]
yep, the gates can only be on for a tiny amount of time so the draw is super small... 50ma or so

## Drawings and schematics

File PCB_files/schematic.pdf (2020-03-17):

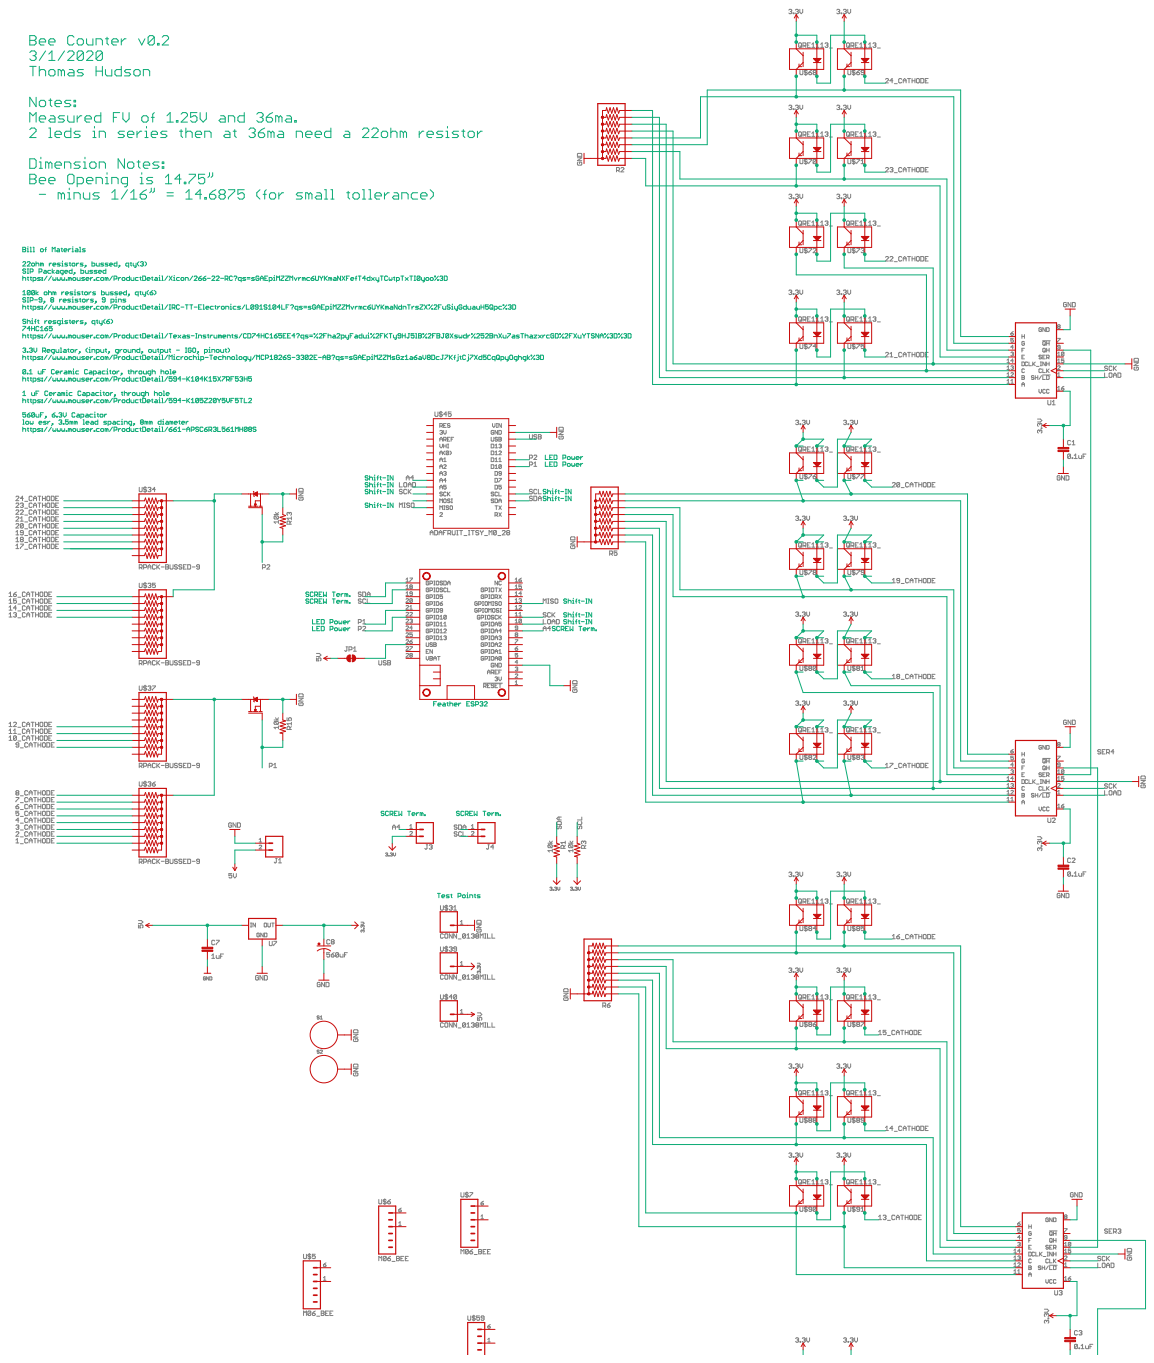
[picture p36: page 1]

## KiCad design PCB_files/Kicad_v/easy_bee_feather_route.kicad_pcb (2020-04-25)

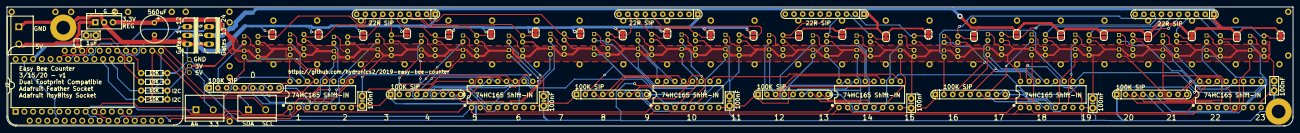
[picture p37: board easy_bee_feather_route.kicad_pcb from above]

Board: 2 copper layers, 373.4 x 34.5 mm, 145 parts (0 on the bottom side), 115 nets.

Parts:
C1, C2, C3, C4, C5, C6: 0.1uF; CAP-PTH-SMALL-KIT
C7: 1uF; CAP-PTH-SMALL-KIT
C8: 560uF; E3,5-8
J1, J3, J4: CONN_025MM; SCREWTERMINAL-5MM-2
J2: ItsyBitsy_M0_M4; DIP-28_W15.24mm
JP1: JUMPER-SMT_2_NC_TRACE_SILK; SMT-JUMPER_2_NC_TRACE_SILK
JP2, JP3, JP4, JP5, JP6, JP7, JP8, JP9, JP10, JP11, JP12, JP13, JP14, JP15, JP16, JP17, JP18, JP19, JP20, JP21, JP22, JP23, JP24, JP25: SolderJumper_2_Open; SolderJumper-2_P1.3mm_Open_RoundedPad1.0x1.5mm
MS2: FEATHERWING_NODIM; FEATHERWING_DIM
Q6, Q7: 60V/32A/35mΩ; TO220V
R1, R3, R4, R13: 10k; AXIAL-0.3
R2, R5, R6, R7, R11, R12: RPACK-BUSSED-8-SIP-PTH-8; RPACK-SIP-PTH-8
S1, S2: STANDOFF_ELECTRICAL5-32; STANDOFF_ELECTRICAL_5_32
U1, U2, U3, U4, U5, U6: 74165; DIP16
U7: V_REG_78XXSINK; TO220-IGO
U$1, U$2, U$3, U$4, U$5, U$6, U$7, U$8, U$9, U$10, U$11, U$12, U$13, U$14, U$15, U$16, U$17, U$18, U$19, U$20, U$21, U$22, U$23, U$24, U$25, U$26, U$27, U$28, U$29, U$30, U$59: M06_BEE; 1X06_BEE
U$31, U$39, U$40: CONN_0138MILL; 1X01-40MILL
U$34, U$35, U$36, U$37: RPACK-BUSSED-9; RPACK-SIP-PTH-9
U$68, U$69, U$70, U$71, U$72, U$73, U$74, U$75, U$76, U$77, U$78, U$79, U$80, U$81, U$82, U$83, U$84, U$85, U$86, U$87, U$88, U$89, U$90, U$91, U$92, U$93, U$94, U$95, U$96, U$97, U$98, U$99, U$100, U$101, U$102, U$103, U$104, U$105, U$106, U$107, U$108, U$109, U$110, U$111, U$112, U$113, U$114, U$115: QRE1113_; DIP400W50P180L360H200Q4

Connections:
3.3V: C1.1, C2.1, C3.1, C4.1, C5.1, C6.1, C8.+, J3.2, R1.P$2, R3.P$2, U1.16, U2.16, U3.16, U4.16, U5.16, U6.16, U7.OUT, U$39.1, U$68.1, U$68.3, U$69.3, U$70.1, U$70.3, U$71.3, U$72.1, U$72.3, U$73.3, U$74.1, U$74.3, U$75.3, U$76.1, U$76.3, U$77.3, U$78.1, U$78.3, U$79.3, U$80.1, U$80.3, U$81.3, U$82.1, U$82.3, U$83.3, U$84.1, U$84.3, U$85.3, U$86.1, U$86.3, U$87.3, U$88.1, U$88.3, U$89.3, U$90.1, U$90.3, U$91.3, U$92.1, U$92.3, U$93.3, U$94.1, U$94.3, U$95.3, U$96.1, U$96.3, U$97.3, U$98.1, U$98.3, U$99.3, U$100.1, U$100.3, U$101.3, U$102.1, U$102.3, U$103.3, U$104.1, U$104.3, U$105.3, U$106.1, U$106.3, U$107.3, U$108.1, U$108.3, U$109.3, U$110.1, U$110.3, U$111.3, U$112.1, U$112.3, U$113.3, U$114.1, U$114.3, U$115.3
5V: C7.1, J1.2, JP1.1, U7.IN, U$40.1
/1_CATHODE: JP2.1, U$36.P$9, U$115.2
/2_CATHODE: JP3.1, U$36.P$8, U$113.2
/3_CATHODE: JP4.1, U$36.P$7, U$111.2
/4_CATHODE: JP5.1, U$36.P$6, U$109.2
/5_CATHODE: JP6.1, U$36.P$5, U$107.2
/6_CATHODE: JP7.1, U$36.P$4, U$105.2
/7_CATHODE: JP8.1, U$36.P$3, U$103.2
/8_CATHODE: JP9.1, U$36.P$2, U$101.2
/9_CATHODE: JP25.2, U$37.P$9, U$99.2
/10_CATHODE: JP24.2, U$37.P$8, U$97.2
/11_CATHODE: JP23.2, U$37.P$7, U$95.2
/12_CATHODE: JP22.2, U$37.P$6, U$93.2
/13_CATHODE: JP21.2, U$35.P$5, U$91.2
/14_CATHODE: JP20.2, U$35.P$4, U$89.2
/15_CATHODE: JP19.2, U$35.P$3, U$87.2
/16_CATHODE: JP18.2, U$35.P$2, U$85.2
/17_CATHODE: JP17.2, U$34.P$9, U$83.2
/18_CATHODE: JP16.2, U$34.P$8, U$81.2
/19_CATHODE: JP15.2, U$34.P$7, U$79.2
/20_CATHODE: JP14.2, U$34.P$6, U$77.2
/21_CATHODE: JP13.2, U$34.P$5, U$75.2
/22_CATHODE: JP12.2, U$34.P$4, U$73.2
/23_CATHODE: JP11.2, U$34.P$3, U$71.2
/24_CATHODE: JP10.2, U$34.P$2, U$69.2
/A4: J2.9, J3.1, MS2.9
/LOAD: J2.10, MS2.10, U1.1, U2.1, U3.1, U4.1, U5.1, U6.1
/MISO: J2.13, MS2.13, U6.9
/P1: J2.22, MS2.21, Q7.1, R4.P$2
/P2: J2.23, MS2.22, Q6.1, R13.P$2
/SCK: MS2.11, U1.2, U2.2, U3.2, U4.2, U5.2, U6.2
/SCL: J2.18, J4.2, MS2.18, R3.P$1
/SDA: J2.17, J4.1, MS2.17, R1.P$1
/SER1: U5.9, U6.10
/SER2: U4.9, U5.10
/SER3: U2.9, U3.10
/SER4: U1.9, U2.10
/USB: J2.26, JP1.2, MS2.26
GND: C1.2, C2.2, C3.2, C4.2, C5.2, C6.2, C7.2, C8.-, J1.1, J2.27, MS2.4, Q6.3, Q7.3, R2.P$1, R4.P$1, R5.P$1, R6.P$1, R7.P$1, R11.P$1, R12.P$1, R13.P$1, S1.P1, S2.P1, U1.8, U1.15, U2.8, U2.15, U3.8, U3.15, U4.8, U4.15, U5.8, U5.15, U6.8, U6.15, U7.GND, U$31.1
unnamed: JP2.2, JP3.2, JP4.2, JP5.2, JP6.2, JP7.2, JP8.2, JP9.2, JP22.1, JP23.1, JP24.1, JP25.1, Q7.2, U$36.P$1, U$37.P$1
unnamed: JP10.1, JP11.1, JP12.1, JP13.1, JP14.1, JP15.1, JP16.1, JP17.1, JP18.1, JP19.1, JP20.1, JP21.1, Q6.2, U$34.P$1, U$35.P$1
unnamed: R2.P$2, U1.3, U$70.4
unnamed: R2.P$3, U1.4, U$71.4
unnamed: R2.P$4, U1.6, U$69.4
unnamed: R2.P$5, U1.5, U$68.4
unnamed: R2.P$6, U1.14, U$73.4
unnamed: R2.P$7, U1.13, U$72.4
unnamed: R2.P$8, U1.12, U$75.4
unnamed: R2.P$9, U1.11, U$74.4
unnamed: R5.P$2, U2.11, U$82.4
unnamed: R5.P$3, U2.12, U$83.4
unnamed: R5.P$4, U2.13, U$80.4
unnamed: R5.P$5, U2.14, U$81.4
unnamed: R5.P$6, U2.3, U$78.4
unnamed: R5.P$7, U2.4, U$79.4
unnamed: R5.P$8, U2.5, U$76.4
unnamed: R5.P$9, U2.6, U$77.4
unnamed: R6.P$2, U3.12, U$91.4
unnamed: R6.P$3, U3.11, U$90.4
unnamed: R6.P$4, U3.13, U$88.4
unnamed: R6.P$5, U3.14, U$89.4
unnamed: R6.P$6, U3.3, U$86.4
unnamed: R6.P$7, U3.4, U$87.4
unnamed: R6.P$8, U3.5, U$84.4
unnamed: R6.P$9, U3.6, U$85.4
unnamed: R7.P$2, U4.11, U$98.4
unnamed: R7.P$3, U4.12, U$99.4
unnamed: R7.P$4, U4.13, U$96.4
unnamed: R7.P$5, U4.14, U$97.4
unnamed: R7.P$6, U4.3, U$94.4
unnamed: R7.P$7, U4.4, U$95.4
unnamed: R7.P$8, U4.5, U$92.4
unnamed: R7.P$9, U4.6, U$93.4
unnamed: R11.P$2, U5.11, U$106.4
unnamed: R11.P$3, U5.12, U$107.4
unnamed: R11.P$4, U5.13, U$104.4
unnamed: R11.P$5, U5.14, U$105.4
unnamed: R11.P$6, U5.3, U$102.4
unnamed: R11.P$7, U5.4, U$103.4
unnamed: R11.P$8, U5.5, U$100.4
unnamed: R11.P$9, U5.6, U$101.4
unnamed: R12.P$2, U6.12, U$115.4
unnamed: R12.P$3, U6.11, U$114.4
unnamed: R12.P$4, U6.13, U$112.4
unnamed: R12.P$5, U6.14, U$113.4
unnamed: R12.P$6, U6.3, U$110.4
unnamed: R12.P$7, U6.4, U$111.4
unnamed: R12.P$8, U6.5, U$108.4
unnamed: R12.P$9, U6.6, U$109.4
unnamed: U3.9, U4.10
unnamed: U$68.2, U$69.1
unnamed: U$70.2, U$71.1
unnamed: U$72.2, U$73.1
unnamed: U$74.2, U$75.1
unnamed: U$76.2, U$77.1
unnamed: U$78.2, U$79.1
unnamed: U$80.2, U$81.1
unnamed: U$82.2, U$83.1
unnamed: U$84.2, U$85.1
unnamed: U$86.2, U$87.1
unnamed: U$88.2, U$89.1
unnamed: U$90.2, U$91.1
unnamed: U$92.2, U$93.1
unnamed: U$94.2, U$95.1
unnamed: U$96.2, U$97.1
unnamed: U$98.2, U$99.1
unnamed: U$100.2, U$101.1
unnamed: U$102.2, U$103.1
unnamed: U$104.2, U$105.1
unnamed: U$106.2, U$107.1
unnamed: U$108.2, U$109.1
unnamed: U$110.2, U$111.1
unnamed: U$112.2, U$113.1
unnamed: U$114.2, U$115.1

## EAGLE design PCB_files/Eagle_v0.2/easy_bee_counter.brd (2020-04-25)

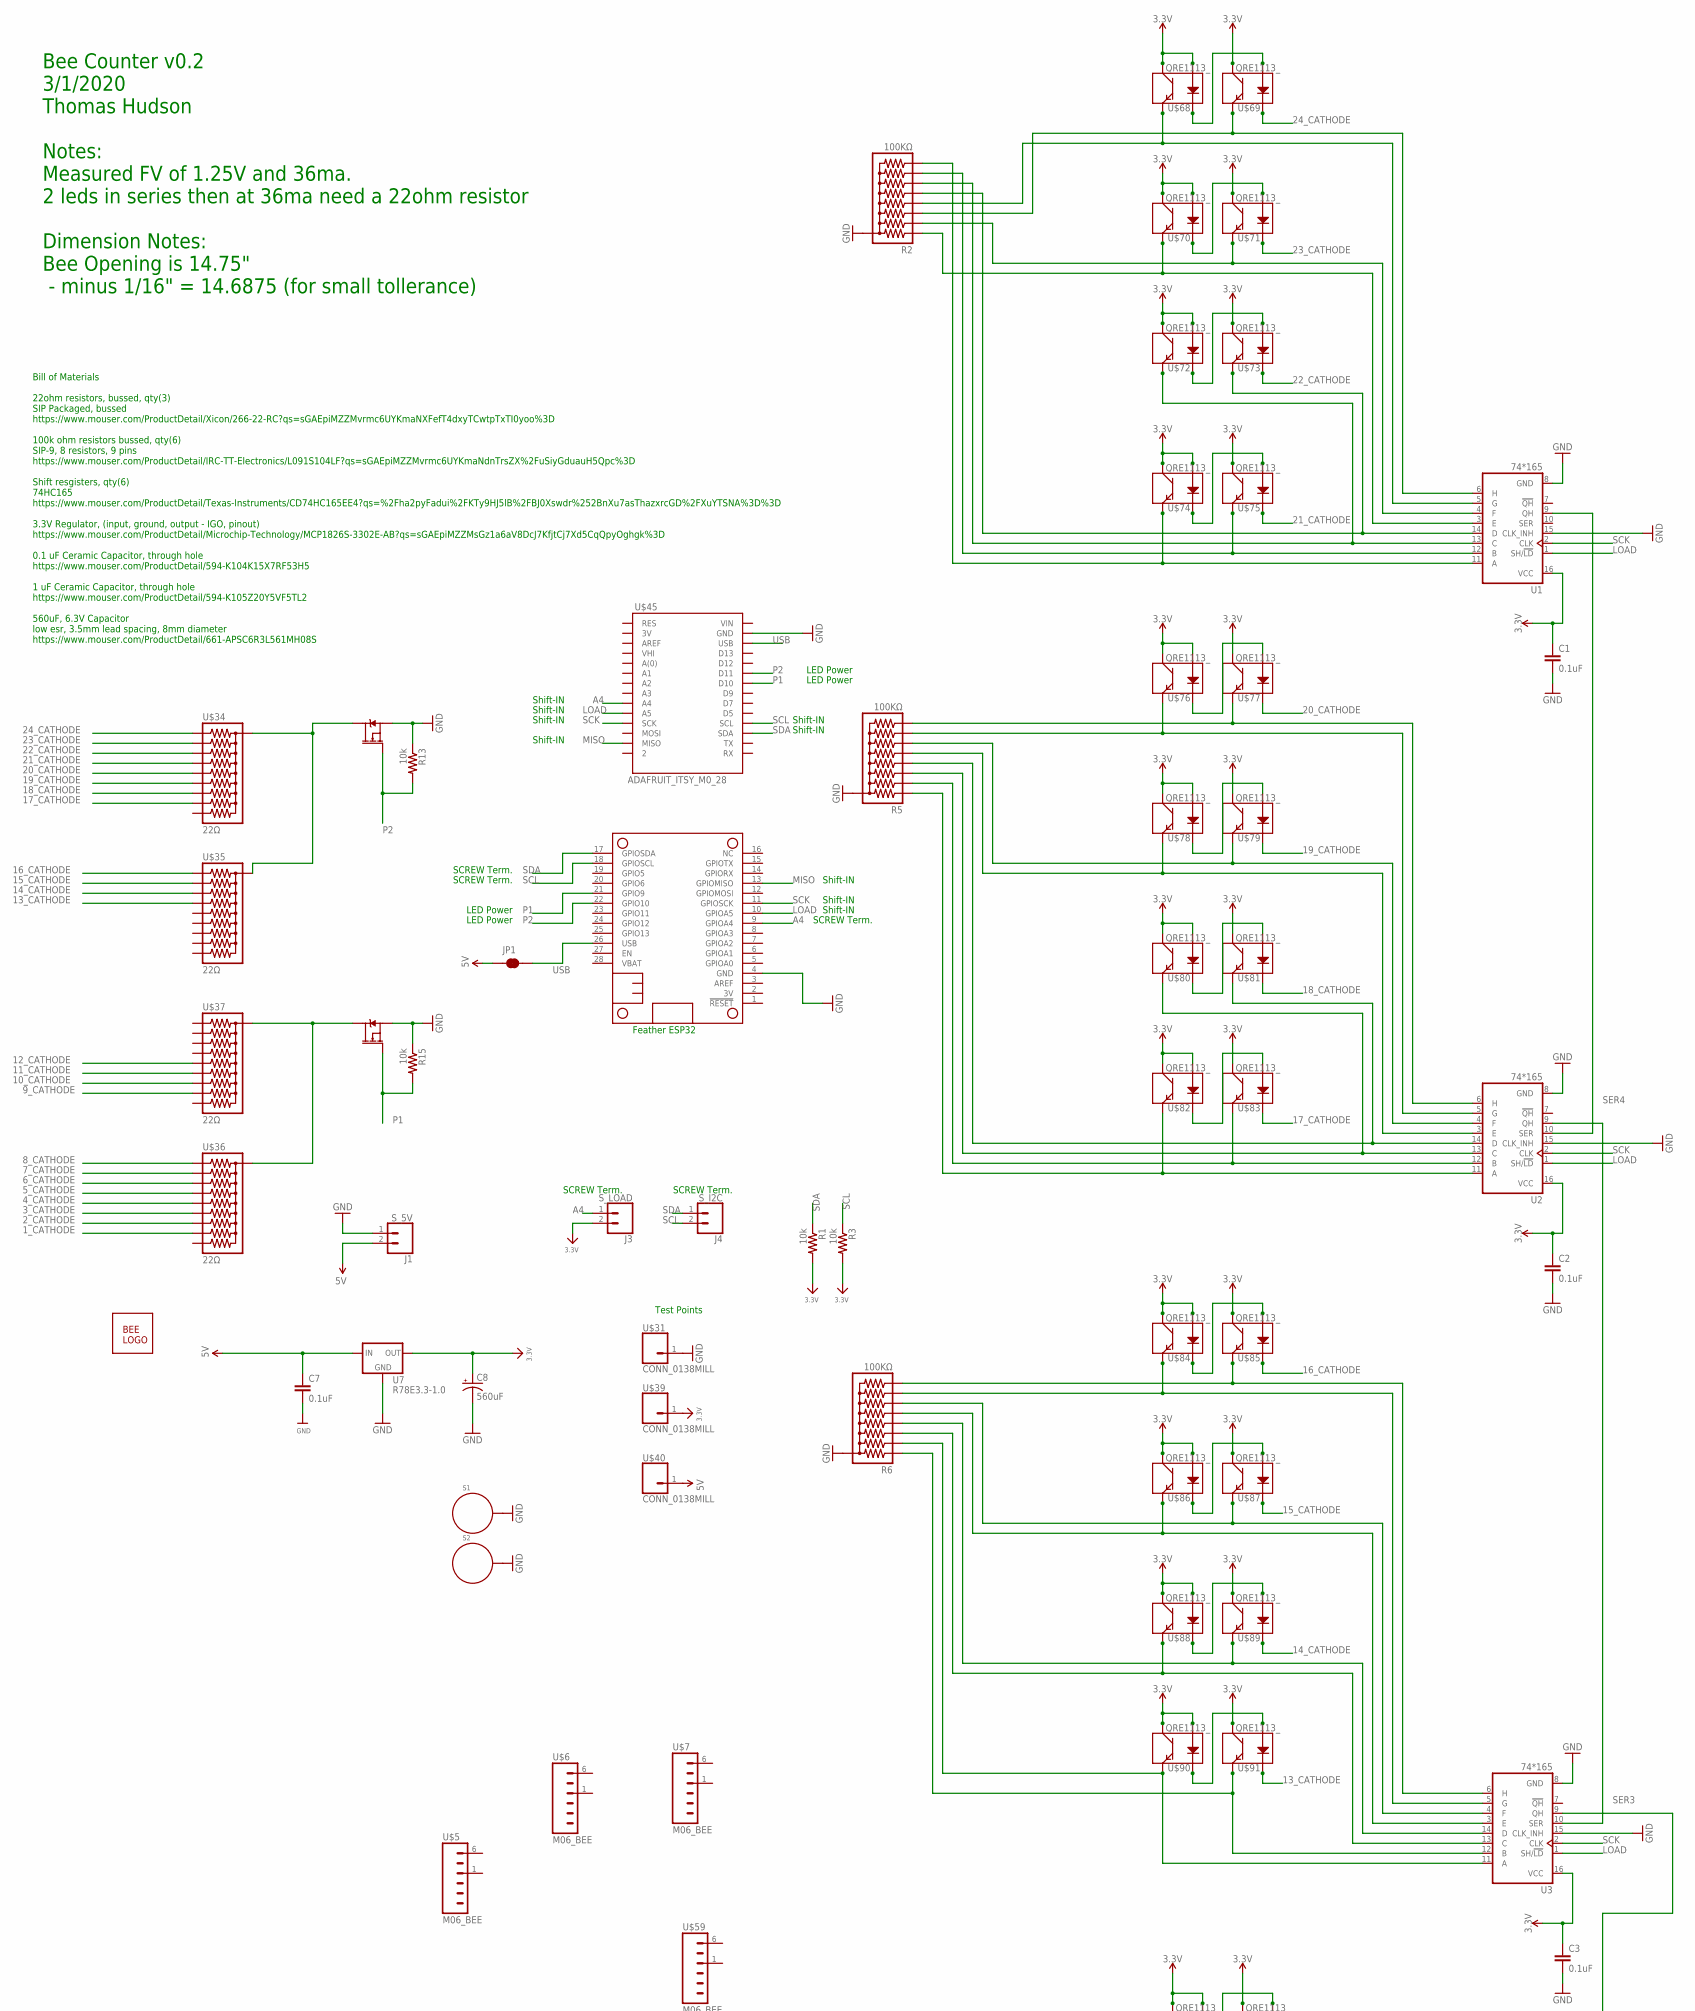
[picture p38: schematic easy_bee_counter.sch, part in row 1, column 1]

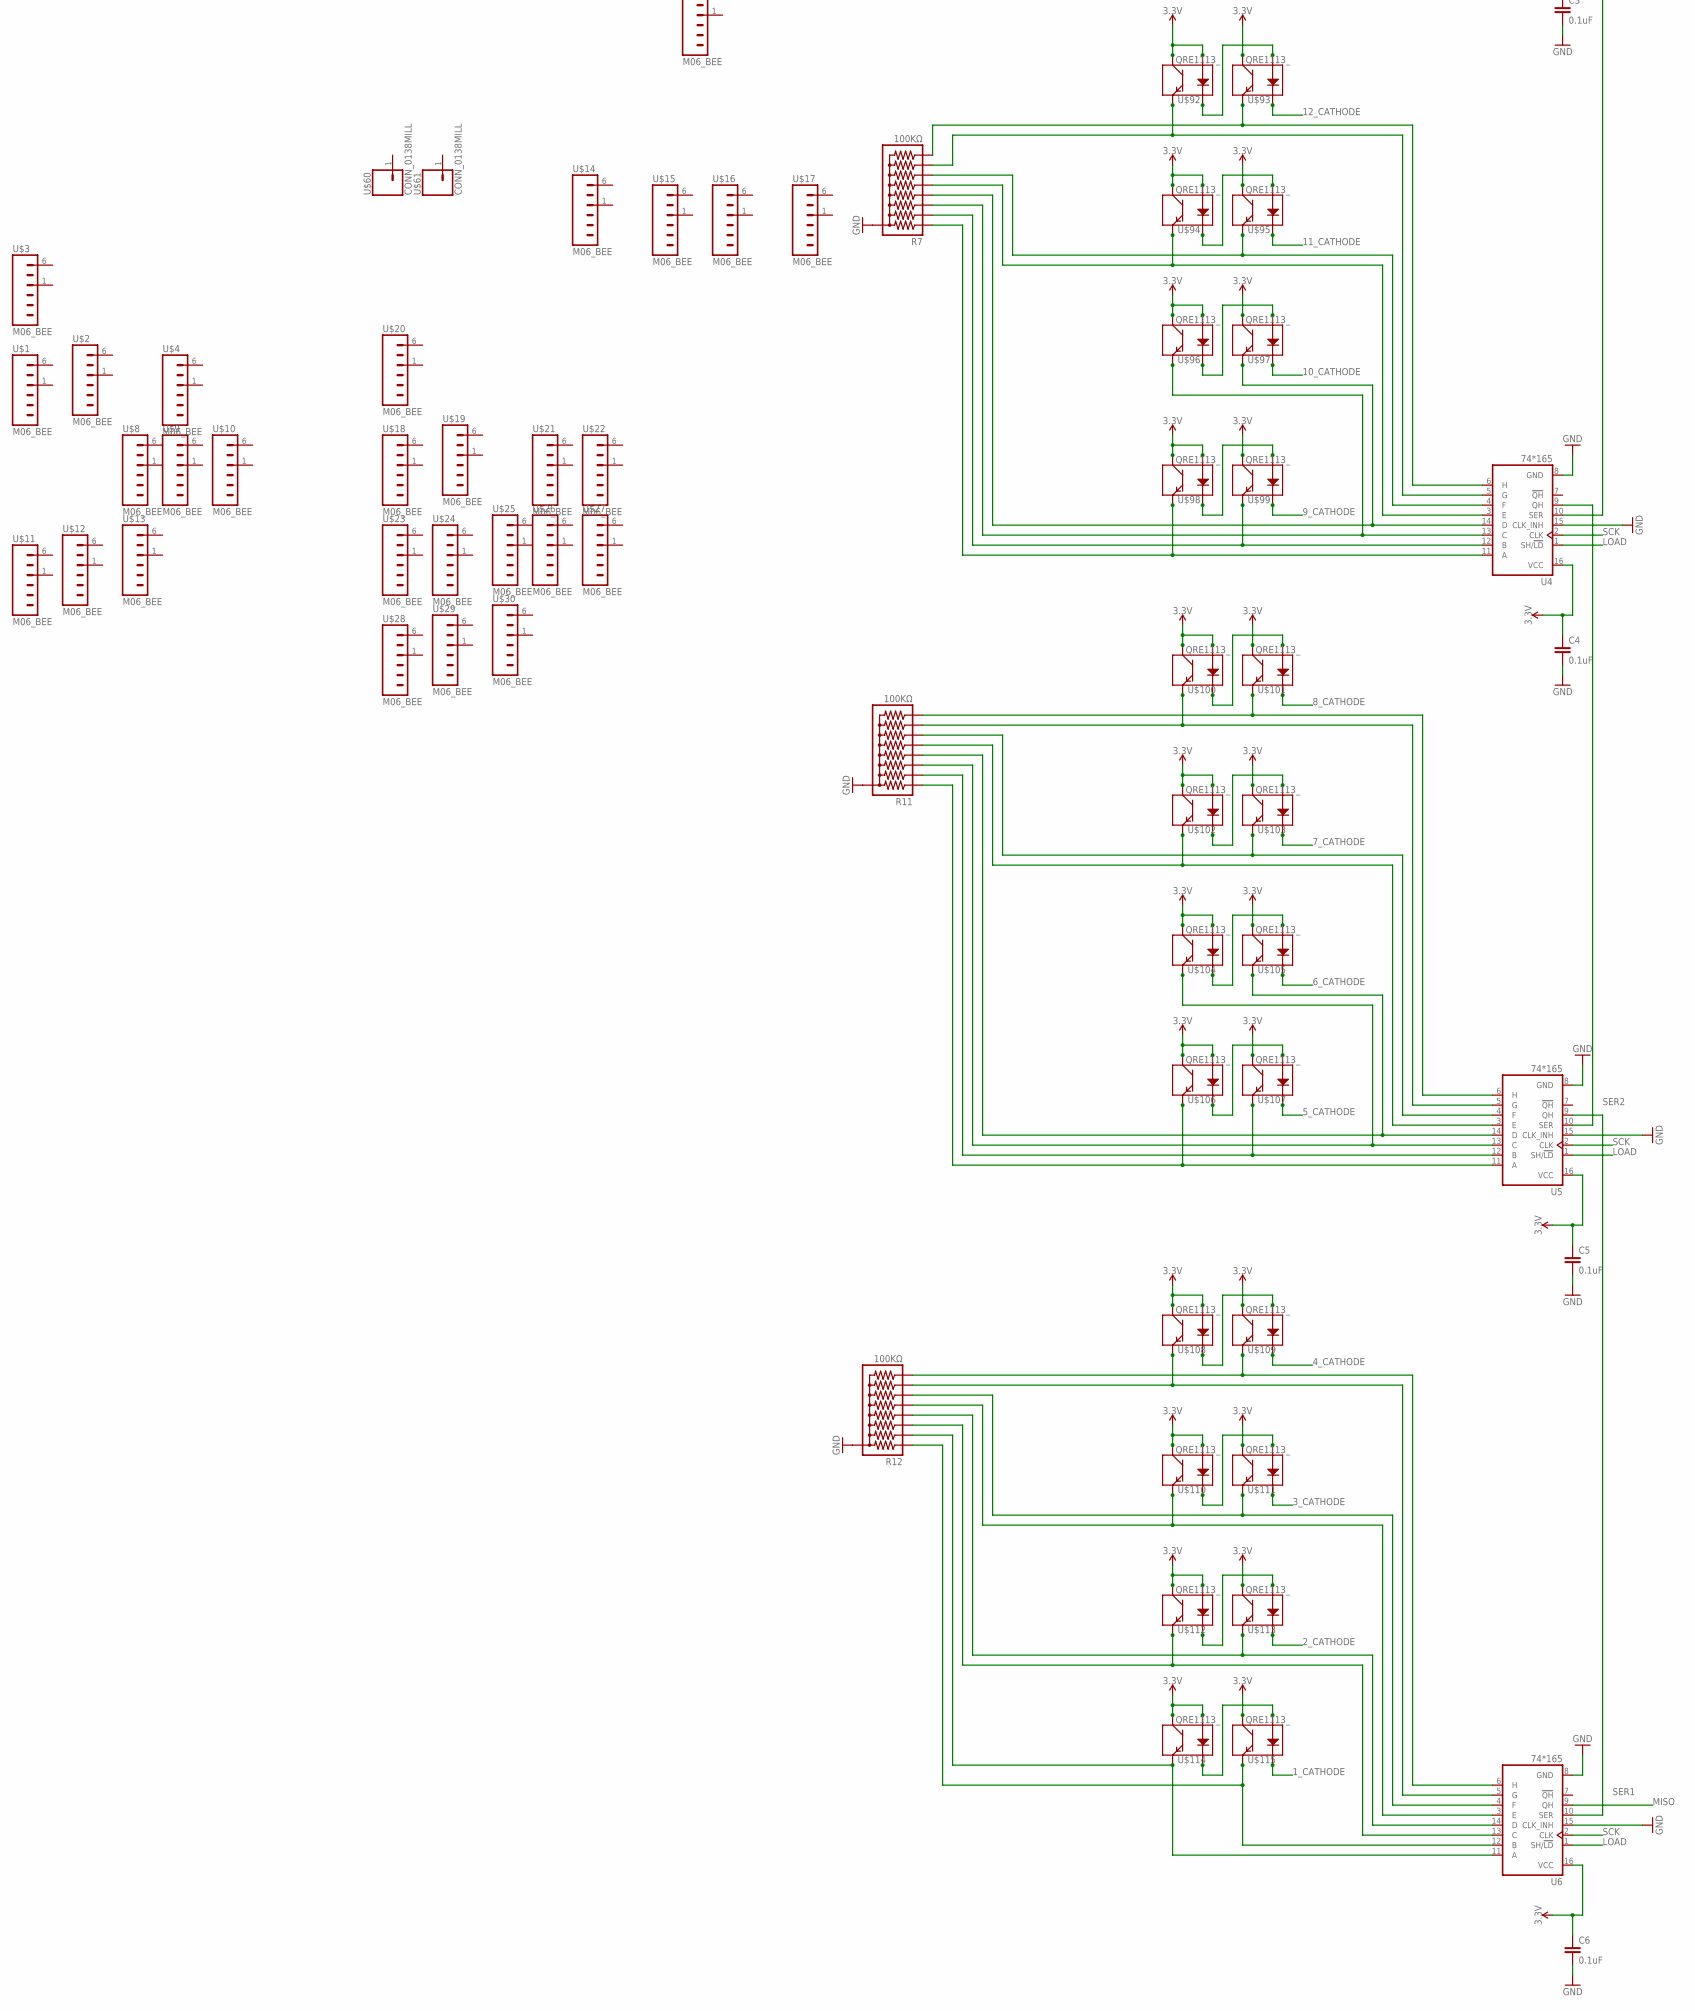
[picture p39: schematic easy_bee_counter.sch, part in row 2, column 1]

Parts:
C1, C2, C3, C4, C5, C6, C7: 0.1uF; CAP-PTH-SMALL-KIT
C8: 560uF; E3,5-8
J1: S_5V; SCREWTERMINAL-5MM-2
J3: S_LOAD; SCREWTERMINAL-5MM-2
J4: S_I2C; SCREWTERMINAL-5MM-2
JP1: JUMPER-SMT_2_NC_TRACE_SILK; SMT-JUMPER_2_NC_TRACE_SILK
MS2: FEATHERWING_NODIM; FEATHERWING_DIM
Q6, Q7: 60V/32A/35mΩ; TO220V
R1, R3, R13, R15: 10k; AXIAL-0.3
R2, R5, R6, R7, R11, R12: 100KΩ; RPACK-SIP-PTH-8
S1, S2: STANDOFF_ELECTRICAL5-32; STANDOFF_ELECTRICAL_5_32
U1, U2, U3, U4, U5, U6: 74*165; DIP16
U7: R78E3.3-1.0; DC-DC_CONVERTER_78XX
U$1, U$2, U$3, U$4, U$5, U$6, U$7, U$8, U$9, U$10, U$11, U$12, U$13, U$14, U$15, U$16, U$17, U$18, U$19, U$20, U$21, U$22, U$23, U$24, U$25, U$26, U$27, U$28, U$29, U$30, U$59: M06_BEE; 1X06_BEE
U$31, U$39, U$40, U$60, U$61: CONN_0138MILL; 1X01-40MILL
U$34, U$35, U$36, U$37: 22Ω; RPACK-SIP-PTH-9
U$44: BEE_LOGO
U$45: ADAFRUIT_ITSY_M0_28; ADAFRUIT_ITS_MO_28
U$68, U$69, U$70, U$71, U$72, U$73, U$74, U$75, U$76, U$77, U$78, U$79, U$80, U$81, U$82, U$83, U$84, U$85, U$86, U$87, U$88, U$89, U$90, U$91, U$92, U$93, U$94, U$95, U$96, U$97, U$98, U$99, U$100, U$101, U$102, U$103, U$104, U$105, U$106, U$107, U$108, U$109, U$110, U$111, U$112, U$113, U$114, U$115: QRE1113_; DIP400W50P180L360H200Q4

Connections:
1_CATHODE: U$36.P$9 (9), U$115.2 (K)
2_CATHODE: U$36.P$8 (8), U$113.2 (K)
3.3V: C1.1, C2.1, C3.1, C4.1, C5.1, C6.1, C8.+, J3.2, R1.P$2 (2), R3.P$2 (2), U1.16 (VCC), U2.16 (VCC), U3.16 (VCC), U4.16 (VCC), U5.16 (VCC), U6.16 (VCC), U7.VOUT (OUT), U$39.1, U$68.1 (A), U$68.3 (C), U$69.3 (C), U$70.1 (A), U$70.3 (C), U$71.3 (C), U$72.1 (A), U$72.3 (C), U$73.3 (C), U$74.1 (A), U$74.3 (C), U$75.3 (C), U$76.1 (A), U$76.3 (C), U$77.3 (C), U$78.1 (A), U$78.3 (C), U$79.3 (C), U$80.1 (A), U$80.3 (C), U$81.3 (C), U$82.1 (A), U$82.3 (C), U$83.3 (C), U$84.1 (A), U$84.3 (C), U$85.3 (C), U$86.1 (A), U$86.3 (C), U$87.3 (C), U$88.1 (A), U$88.3 (C), U$89.3 (C), U$90.1 (A), U$90.3 (C), U$91.3 (C), U$92.1 (A), U$92.3 (C), U$93.3 (C), U$94.1 (A), U$94.3 (C), U$95.3 (C), U$96.1 (A), U$96.3 (C), U$97.3 (C), U$98.1 (A), U$98.3 (C), U$99.3 (C), U$100.1 (A), U$100.3 (C), U$101.3 (C), U$102.1 (A), U$102.3 (C), U$103.3 (C), U$104.1 (A), U$104.3 (C), U$105.3 (C), U$106.1 (A), U$106.3 (C), U$107.3 (C), U$108.1 (A), U$108.3 (C), U$109.3 (C), U$110.1 (A), U$110.3 (C), U$111.3 (C), U$112.1 (A), U$112.3 (C), U$113.3 (C), U$114.1 (A), U$114.3 (C), U$115.3 (C)
3_CATHODE: U$36.P$7 (7), U$111.2 (K)
4_CATHODE: U$36.P$6 (6), U$109.2 (K)
5V: C7.1, J1.2, JP1.1, U7.VIN (IN), U$40.1
5_CATHODE: U$36.P$5 (5), U$107.2 (K)
6_CATHODE: U$36.P$4 (4), U$105.2 (K)
7_CATHODE: U$36.P$3 (3), U$103.2 (K)
8_CATHODE: U$36.P$2 (2), U$101.2 (K)
9_CATHODE: U$37.P$9 (9), U$99.2 (K)
10_CATHODE: U$37.P$8 (8), U$97.2 (K)
11_CATHODE: U$37.P$7 (7), U$95.2 (K)
12_CATHODE: U$37.P$6 (6), U$93.2 (K)
13_CATHODE: U$35.P$5 (5), U$91.2 (K)
14_CATHODE: U$35.P$4 (4), U$89.2 (K)
15_CATHODE: U$35.P$3 (3), U$87.2 (K)
16_CATHODE: U$35.P$2 (2), U$85.2 (K)
17_CATHODE: U$34.P$9 (9), U$83.2 (K)
18_CATHODE: U$34.P$8 (8), U$81.2 (K)
19_CATHODE: U$34.P$7 (7), U$79.2 (K)
20_CATHODE: U$34.P$6 (6), U$77.2 (K)
21_CATHODE: U$34.P$5 (5), U$75.2 (K)
22_CATHODE: U$34.P$4 (4), U$73.2 (K)
23_CATHODE: U$34.P$3 (3), U$71.2 (K)
24_CATHODE: U$34.P$2 (2), U$69.2 (K)
A4: J3.1, MS2.9 (GPIOA4), U$45.A4
GND: C1.2, C2.2, C3.2, C4.2, C5.2, C6.2, C7.2, C8.-, J1.1, MS2.4 (GND), Q6.3 (S), Q7.3 (S), R2.P$1 (1), R5.P$1 (1), R6.P$1 (1), R7.P$1 (1), R11.P$1 (1), R12.P$1 (1), R13.P$1 (1), R15.P$1 (1), S1.P1, S2.P1, U1.8 (GND), U1.15 (CLK_INH), U2.8 (GND), U2.15 (CLK_INH), U3.8 (GND), U3.15 (CLK_INH), U4.8 (GND), U4.15 (CLK_INH), U5.8 (GND), U5.15 (CLK_INH), U6.8 (GND), U6.15 (CLK_INH), U7.GND, U$31.1, U$45.GND
LOAD: MS2.10 (GPIOA5), U1.1 (SH/!LD), U2.1 (SH/!LD), U3.1 (SH/!LD), U4.1 (SH/!LD), U5.1 (SH/!LD), U6.1 (SH/!LD), U$45.A5
MISO: MS2.13 (GPIOMISO), U6.9 (QH), U$45.MISO
unnamed: U$94.2 (K), U$95.1 (A)
unnamed: U$92.2 (K), U$93.1 (A)
unnamed: U$96.2 (K), U$97.1 (A)
unnamed: U$98.2 (K), U$99.1 (A)
unnamed: U$106.2 (K), U$107.1 (A)
unnamed: U$104.2 (K), U$105.1 (A)
unnamed: U$100.2 (K), U$101.1 (A)
unnamed: U$108.2 (K), U$109.1 (A)
unnamed: U$102.2 (K), U$103.1 (A)
unnamed: U$110.2 (K), U$111.1 (A)
unnamed: R5.P$9 (9), U2.6 (H), U$77.4 (E)
unnamed: U$112.2 (K), U$113.1 (A)
unnamed: U$114.2 (K), U$115.1 (A)
unnamed: R6.P$3 (3), U3.11 (A), U$90.4 (E)
unnamed: R6.P$2 (2), U3.12 (B), U$91.4 (E)
unnamed: R6.P$4 (4), U3.13 (C), U$88.4 (E)
unnamed: R12.P$6 (6), U6.3 (E), U$110.4 (E)
unnamed: R6.P$5 (5), U3.14 (D), U$89.4 (E)
unnamed: R6.P$8 (8), U3.5 (G), U$84.4 (E)
unnamed: Q6.2 (D), U$34.P$1 (1), U$35.P$1 (1)
unnamed: R6.P$9 (9), U3.6 (H), U$85.4 (E)
unnamed: R6.P$6 (6), U3.3 (E), U$86.4 (E)
unnamed: R6.P$7 (7), U3.4 (F), U$87.4 (E)
unnamed: R5.P$4 (4), U2.13 (C), U$80.4 (E)
unnamed: R5.P$5 (5), U2.14 (D), U$81.4 (E)
unnamed: R5.P$8 (8), U2.5 (G), U$76.4 (E)
unnamed: U3.9 (QH), U4.10 (SER)
unnamed: R5.P$6 (6), U2.3 (E), U$78.4 (E)
unnamed: R12.P$3 (3), U6.11 (A), U$114.4 (E)
unnamed: R5.P$7 (7), U2.4 (F), U$79.4 (E)
unnamed: R5.P$3 (3), U2.12 (B), U$83.4 (E)
unnamed: R7.P$4 (4), U4.13 (C), U$96.4 (E)
unnamed: R5.P$2 (2), U2.11 (A), U$82.4 (E)
unnamed: R2.P$7 (7), U1.13 (C), U$72.4 (E)
unnamed: R2.P$6 (6), U1.14 (D), U$73.4 (E)
unnamed: R2.P$5 (5), U1.5 (G), U$68.4 (E)
unnamed: R2.P$4 (4), U1.6 (H), U$69.4 (E)
unnamed: R2.P$2 (2), U1.3 (E), U$70.4 (E)
unnamed: R2.P$3 (3), U1.4 (F), U$71.4 (E)
unnamed: R2.P$8 (8), U1.12 (B), U$75.4 (E)
unnamed: R2.P$9 (9), U1.11 (A), U$74.4 (E)
unnamed: U$68.2 (K), U$69.1 (A)
unnamed: U$70.2 (K), U$71.1 (A)
unnamed: U$72.2 (K), U$73.1 (A)
unnamed: U$74.2 (K), U$75.1 (A)
unnamed: U$82.2 (K), U$83.1 (A)
unnamed: U$80.2 (K), U$81.1 (A)
unnamed: U$76.2 (K), U$77.1 (A)
unnamed: U$78.2 (K), U$79.1 (A)
unnamed: U$84.2 (K), U$85.1 (A)
unnamed: U$86.2 (K), U$87.1 (A)
unnamed: U$88.2 (K), U$89.1 (A)
unnamed: U$90.2 (K), U$91.1 (A)
unnamed: R12.P$7 (7), U6.4 (F), U$111.4 (E)
unnamed: R7.P$8 (8), U4.5 (G), U$92.4 (E)
unnamed: Q7.2 (D), U$36.P$1 (1), U$37.P$1 (1)
unnamed: R7.P$6 (6), U4.3 (E), U$94.4 (E)
unnamed: R7.P$2 (2), U4.11 (A), U$98.4 (E)
unnamed: R11.P$3 (3), U5.12 (B), U$107.4 (E)
unnamed: R12.P$2 (2), U6.12 (B), U$115.4 (E)
unnamed: R11.P$4 (4), U5.13 (C), U$104.4 (E)
unnamed: R11.P$8 (8), U5.5 (G), U$100.4 (E)
unnamed: R11.P$6 (6), U5.3 (E), U$102.4 (E)
unnamed: R11.P$2 (2), U5.11 (A), U$106.4 (E)
unnamed: R12.P$4 (4), U6.13 (C), U$112.4 (E)
unnamed: R12.P$5 (5), U6.14 (D), U$113.4 (E)
unnamed: R11.P$5 (5), U5.14 (D), U$105.4 (E)
unnamed: R12.P$8 (8), U6.5 (G), U$108.4 (E)
unnamed: R12.P$9 (9), U6.6 (H), U$109.4 (E)
unnamed: R11.P$9 (9), U5.6 (H), U$101.4 (E)
unnamed: R11.P$7 (7), U5.4 (F), U$103.4 (E)
unnamed: R7.P$5 (5), U4.14 (D), U$97.4 (E)
unnamed: R7.P$9 (9), U4.6 (H), U$93.4 (E)
unnamed: R7.P$7 (7), U4.4 (F), U$95.4 (E)
unnamed: R7.P$3 (3), U4.12 (B), U$99.4 (E)
P1: MS2.21 (GPIO9), Q7.1 (G), R15.P$2 (2), U$45.D10
P2: MS2.22 (GPIO10), Q6.1 (G), R13.P$2 (2), U$45.D11
SCK: MS2.11 (GPIOSCK), U1.2 (CLK), U2.2 (CLK), U3.2 (CLK), U4.2 (CLK), U5.2 (CLK), U6.2 (CLK), U$45.SCK
SCL: J4.2, MS2.18 (GPIOSCL), R3.P$1 (1), U$45.SCL
SDA: J4.1, MS2.17 (GPIOSDA), R1.P$1 (1), U$45.SDA
SER1: U5.9 (QH), U6.10 (SER)
SER2: U4.9 (QH), U5.10 (SER)
SER3: U2.9 (QH), U3.10 (SER)
SER4: U1.9 (QH), U2.10 (SER)
USB: JP1.2, MS2.26 (USB), U$45.USB

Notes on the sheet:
Notes: Measured FV of 1.25V and 36ma. 2 leds in series then at 36ma need a 22ohm resistor Dimension Notes: Bee Opening is 14.75" - minus 1/16" = 14.6875 (for small tollerance)
Bill of Materials 22ohm resistors, bussed, qty(3) SIP Packaged, bussed https://www.mouser.com/ProductDetail/Xicon/266-22-RC?qs=sGAEpiMZZMvrmc6UYKmaNXFefT4dxyTCwtpTxTI0yoo%3D 100k ohm resistors bussed, qty(6) SIP-9, 8 resistors, 9 pins https://www.mouser.com/ProductDetail/IRC-TT-Electronics/L091S104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
Shift-IN
LED Power
SCREW Term.
Test Points
Feather ESP32
Bee Counter v0.2 3/1/2020 Thomas Hudson

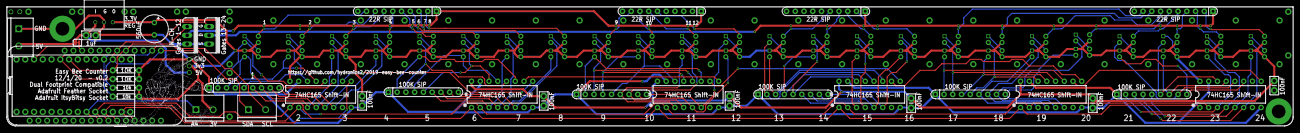
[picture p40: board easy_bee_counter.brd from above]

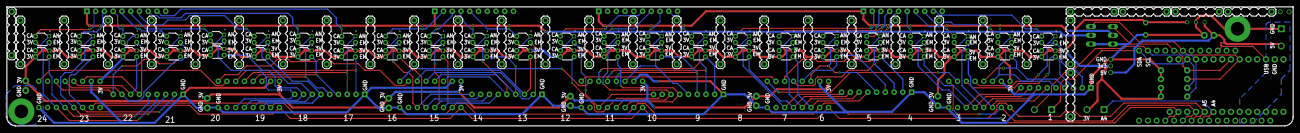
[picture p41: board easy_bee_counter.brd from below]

Board: 2 copper layers, 373.4 x 34.5 mm, 124 parts (79 on the bottom side), 115 nets.

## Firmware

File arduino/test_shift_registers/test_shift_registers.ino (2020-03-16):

/*
 * For more help on reading shift registers: http://www.gammon.com.au/forum/?id=11979
 *  
 *   gate     0   ||  1  ||  2  ||  3  ||  4   ||   5  ||  6   ||  7   ||  8   ||  9   ||  10  ||  11  ||  12  ||  13  ||  14  ||  15  ||  16  ||  17  ||  18  ||  19  ||  20  ||  21  ||  22  ||  23
 *   inside   1   ||  3  ||  5  ||  7  ||  9   ||  11  ||  13  ||  15  ||  17  ||  19  ||  21  ||  23  ||  25  ||  27  ||  29  ||  31  ||  33  ||  35  ||  37  ||  39  ||  41  ||  43  ||  45  ||  47
 *   outside  2   ||  4  ||  6  ||  8  ||  10  ||  12  ||  14  ||  16  ||  18  ||  20  ||  22  ||  24  ||  26  ||  28  ||  30  ||  32  ||  34  ||  36  ||  38  ||  40  ||  42  ||  44  ||  46  ||  48
 * 
 *  HOW long can we drive the LEDs ON without current limiting resistors?
 *  LED timed pulse (tp) allowance vs period (T)
 *  with increasing forward current the IR LED cutsheet says max tp/T = 0.01
 *  so the max tp for 1 amp is 100us and 100us/0.01 = 10ms
 *  with an ON time of ~75us the max period or delay between ON times is 75us/0.01=7.5ms
 *  So the minimum OFF time between ON times is 7.5ms
 *  This is very conservative as the forward voltage of 3.3v/2 = 1.65v, and max current from the cutsheet is estimated ~170ma 
 *  this is well below the absolute max of 1 amp with which the tp/T ratio was developed for
 *  
 */


#include <SPI.h>

const int LATCH = A5; 

//Pins Feather ESP32
const byte powerGates1 = 15;
const byte powerGates2 = 33;

//Pins ItsyBitsy
//const byte powerGates1 = 10;
//const byte powerGates2 = 11;

void setup ()
{
  
  SPI.begin();
  SPI.beginTransaction(SPISettings(3000000, MSBFIRST, SPI_MODE2)); //3Mhz
  //Reading 24 bits (all sensors) at 1Mhz should take about 24 microseconds,
  //reading 24 bits (all sensors) at 3Mhz should take about 8us
  
  Serial.begin (115200);
  Serial.println ("Begin switch test.");
  pinMode (LATCH, OUTPUT);
  digitalWrite (LATCH, HIGH);

  pinMode (powerGates1, OUTPUT);
  digitalWrite(powerGates1, LOW);
  pinMode (powerGates2, OUTPUT);
  digitalWrite(powerGates2, LOW);
  
}  // end of setup

byte switchBank1;
byte oldSwitchBank1; 
byte switchBank2;
byte oldSwitchBank2; 
byte switchBank3;
byte oldSwitchBank3; 
byte switchBank4;
byte oldSwitchBank4; 
byte switchBank5;
byte oldSwitchBank5; 
byte switchBank6;
byte oldSwitchBank6; 

void loop ()
{
  digitalWrite(powerGates1, HIGH);
  digitalWrite(powerGates2, HIGH);
  delayMicroseconds(75); //first 24 gates only need 15us while gates closer to the end need ~40us-75us
  
  
  digitalWrite (LATCH, LOW);    // pulse the parallel load latch
  delayMicroseconds(3);
  digitalWrite (LATCH, HIGH);

  delayMicroseconds(3);
  
  digitalWrite(powerGates1, LOW);
  digitalWrite(powerGates2, LOW);

  switchBank1 = SPI.transfer (0); //8
  switchBank2 = SPI.transfer (0); //16
  switchBank3 = SPI.transfer (0); //24
  switchBank4 = SPI.transfer (0); //32
  switchBank5 = SPI.transfer (0); //40
  switchBank6 = SPI.transfer (0); //48  
  
  
  byte mask = 1;
  int sensor = 1;
  for (int i = 1; i <= 8; i++)
  {
    if ((switchBank1 & mask) != (oldSwitchBank1 & mask))
      {
      Serial.print ("Switch ");
      Serial.print (sensor);
      Serial.print (" ");
      Serial.println ((switchBank1 & mask) ? "ir triggered" : "none");
      }  // end of bit has changed
    mask <<= 1; 
    sensor++; 
  }  // end of for each bit
  mask = 1;
  sensor = 9;
  for (int i = 1; i <= 8; i++)
  {
    if ((switchBank2 & mask) != (oldSwitchBank2 & mask))
      {
      Serial.print ("Switch ");
      Serial.print (sensor);
      Serial.print (" ");
      Serial.println ((switchBank2 & mask) ? "ir triggered" : "none");
      
      }  // end of bit has changed
    mask <<= 1; 
    sensor++; 
  }  // end of for each bit
  mask = 1;
  sensor = 17;
  for (int i = 1; i <= 8; i++)
  {
    if ((switchBank3 & mask) != (oldSwitchBank3 & mask))
    {
      Serial.print ("Switch ");
      Serial.print (sensor);
      Serial.print (" ");
      Serial.println ((switchBank3 & mask) ? "ir triggered" : "none");
    }  // end of bit has changed
    mask <<= 1;
    sensor++;  
  }  // end of for each bit
  mask = 1;
  sensor = 25;
  for (int i = 1; i <= 8; i++)
  {
    if ((switchBank4 & mask) != (oldSwitchBank4 & mask))
    {
      Serial.print ("Switch ");
      Serial.print (sensor);
      Serial.print (" ");
      Serial.println ((switchBank4 & mask) ? "ir triggered" : "none");
    }  // end of bit has changed
    mask <<= 1; 
    sensor++; 
  }  // end of for each bit
  mask = 1;
  sensor = 33;
  for (int i = 1; i <= 8; i++)
  {
    if ((switchBank5 & mask) != (oldSwitchBank5 & mask))
    {
      Serial.print ("Switch ");
      Serial.print (sensor);
      Serial.print (" ");
      Serial.println ((switchBank5 & mask) ? "ir triggered" : "none");
    }  // end of bit has changed
    mask <<= 1; 
    sensor++; 
  }  // end of for each bit
  mask = 1;
  sensor = 41;
  for (int i = 1; i <= 8; i++)
  {
    if ((switchBank6 & mask) != (oldSwitchBank6 & mask))
    {
      Serial.print ("Switch ");
      Serial.print (sensor);
      Serial.print (" ");
      Serial.println ((switchBank6 & mask) ? "ir triggered" : "none");
    }  // end of bit has changed
    mask <<= 1;  
    sensor++;
  }  // end of for each bit

  oldSwitchBank1 = switchBank1;
  oldSwitchBank2 = switchBank2;
  oldSwitchBank3 = switchBank3;
  oldSwitchBank4 = switchBank4;
  oldSwitchBank5 = switchBank5;
  oldSwitchBank6 = switchBank6;

  delay (20);   // must be greater than 7.5ms (see notes at top of code)
}  // end of loop

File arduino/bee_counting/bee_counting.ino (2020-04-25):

/*
 *  
 *   gate     0   ||  1  ||  2  ||  3  ||  4   ||   5  ||  6   ||  7   ||  8   ||  9   ||  10  ||  11  ||  12  ||  13  ||  14  ||  15  ||  16  ||  17  ||  18  ||  19  ||  20  ||  21  ||  22  ||  23
 *   inside   1   ||  3  ||  5  ||  7  ||  9   ||  11  ||  13  ||  15  ||  17  ||  19  ||  21  ||  23  ||  25  ||  27  ||  29  ||  31  ||  33  ||  35  ||  37  ||  39  ||  41  ||  43  ||  45  ||  47
 *   outside  2   ||  4  ||  6  ||  8  ||  10  ||  12  ||  14  ||  16  ||  18  ||  20  ||  22  ||  24  ||  26  ||  28  ||  30  ||  32  ||  34  ||  36  ||  38  ||  40  ||  42  ||  44  ||  46  ||  48
 * 
 *  
 *  HOW long can we drive the LEDs ON without current limiting resistors?
 *  LED timed pulse (tp) allowance vs period (T)
 *  with increasing forward current the IR LED cutsheet says max tp/T = 0.01
 *  so the max tp for 1 amp is 100us and 100us/0.01 = 10ms
 *  with an ON time of ~75us the max period or delay between ON times is 75us/0.01=7.5ms
 *  So the minimum OFF time between ON times is 7.5ms
 *  This is very conservative as the forward voltage of 3.3v/2 = 1.65v, and max current from the cutsheet is estimated ~170ma 
 *  this is well below the absolute max of 1 amp with which the tp/T ratio was developed for
 *  
 *  
 *  Rough Power Draw with cheap USB current sensor
 *  feather ESP32 by itself with tp/T  15us/2ms => 50ma
 *  feather ESP32 by itself with tp/T  15us/10ms => 40-50ma
 *  ESP32 & LEDs
 *  tp/T  15us/2ms  100ma
 *  tp/T  15us/4ms  75ma
 *  tp/T  15us/6ms  60-70ma had to add 3000uf cap to smooth out drawl
 *  tp/T  15us/8ms  50-60ma had to add 3000uf cap to smooth out drawl
 *  tp/T  15us/10ms  50ma had to add 3000uf cap to smooth out drawl 
 *  
 *  
 *  
 *  
 *  This sketch:
 *  It takes a honey bee around 250ms to traverse the sensor This code only looks for honeybees moving faster than 650ms.
 *  
 *  
 *  
 *  
 */

#include <SPI.h>

const int testLed = 13; //onboard LED
const int LATCH = A5; 

//Pins Feather ESP32
const byte powerGates1 = 15;
const byte powerGates2 = 33;

//Pins ItsyBitsy
//const byte powerGates1 = 10;
//const byte powerGates2 = 11;


const int numberOfGates = 24; // 24 gates, 48 sensors
const int startGate = 0;  //useful for testing
const int endGate = 24;   //useful for testing
const int debeebounce = 30;
const int outputDelay = 15000;  //prints bee counts every 15 seconds
unsigned long lastOutput = 0;
unsigned long currentTime = 0;


//boolean 0 or 1 sensor readings, 1 bee is present
boolean inSensorReading[numberOfGates];
boolean outSensorReading[numberOfGates];

boolean lastInSensorReading[numberOfGates];
boolean lastOutSensorReading[numberOfGates];

boolean checkStateIn[numberOfGates];
boolean checkStateOut[numberOfGates];

int inCount[numberOfGates];
int outCount[numberOfGates];
  
unsigned long startInReadingTime[numberOfGates];
unsigned long startOutReadingTime[numberOfGates];

unsigned long inSensorTime[numberOfGates];
unsigned long outSensorTime[numberOfGates];
 
unsigned long lastInFinishedTime[numberOfGates];
unsigned long lastOutFinishedTime[numberOfGates];
  
unsigned long inReadingTimeHigh[numberOfGates];
unsigned long outReadingTimeHigh[numberOfGates];

unsigned long lastInTime[numberOfGates];
unsigned long lastOutTime[numberOfGates];

unsigned long lastInReadingTimeHigh[numberOfGates];
unsigned long lastOutReadingTimeHigh[numberOfGates];

int totalTimeTravelGoingOut[numberOfGates];
int totalTimeTravelGoingIn[numberOfGates];

int firstTestInVariable[numberOfGates];


int firstTestOutVariable[numberOfGates];


int inTotal;
int outTotal;


int n = 0;



void setup ()
{
  
  SPI.begin();
  SPI.beginTransaction(SPISettings(3000000, MSBFIRST, SPI_MODE2));
  
  Serial.begin (115200);
  Serial.println ("Begin switch test.");
  pinMode (LATCH, OUTPUT);
  digitalWrite (LATCH, HIGH);

  pinMode (powerGates1, OUTPUT);
  digitalWrite(powerGates1, LOW);
  pinMode (powerGates2, OUTPUT);
  digitalWrite(powerGates2, LOW);

  pinMode(testLed, OUTPUT);
  
}  // end of setup

byte switchBank1;
byte oldSwitchBank1; 
byte switchBank2;
byte oldSwitchBank2; 
byte switchBank3;
byte oldSwitchBank3; 
byte switchBank4;
byte oldSwitchBank4; 
byte switchBank5;
byte oldSwitchBank5; 
byte switchBank6;
byte oldSwitchBank6; 
byte switchBank7;
byte oldSwitchBank7; 
byte switchBank8;
byte oldSwitchBank8; 

void loop ()
{
  currentTime = millis();  
  
  digitalWrite(powerGates1, HIGH);
  digitalWrite(powerGates2, HIGH);
  delayMicroseconds(75); //first 24 gates only need 15us while gates closer to the end need ~40us-75us
  
  digitalWrite (LATCH, LOW);    // pulse the parallel load latch
  delayMicroseconds(3);
  digitalWrite (LATCH, HIGH);

  delayMicroseconds(3);
  
  digitalWrite(powerGates1, LOW);
  digitalWrite(powerGates2, LOW);

  //Reading 24 bits at 1Mhz should take about 24 microseconds,
  //reading 24 bits at 3Mhz should take about 8us
  //reading 48 bits at 3Mhz should take abotu 16us
  switchBank1 = SPI.transfer (0); //8
  switchBank2 = SPI.transfer (0); //16
  switchBank3 = SPI.transfer (0); //24
  switchBank4 = SPI.transfer (0); //32
  switchBank5 = SPI.transfer (0); //40
  switchBank6 = SPI.transfer (0); //48  
  
 
  
  if(switchBank1 != oldSwitchBank1 || switchBank2 != oldSwitchBank2 || switchBank3 != oldSwitchBank3 || switchBank4 != oldSwitchBank4 || switchBank5 != oldSwitchBank5 || switchBank6 != oldSwitchBank6)
  {
    //convert bytes to gate values
    int gate = 0;
    for(int i = 0; i < 8; i++)
    {
      if((switchBank1 >> i) & 1)
          outSensorReading[gate] = HIGH;
      else outSensorReading[gate] = LOW;
      i++;
      if((switchBank1 >> i) & 1)
          inSensorReading[gate] = HIGH;
      else inSensorReading[gate] = LOW;       
      gate++;  
    }
    for(int i = 0; i < 8; i++)
    {
      if((switchBank2 >> i) & 1)
          outSensorReading[gate] = HIGH;
      else outSensorReading[gate] = LOW;
      i++;
      if((switchBank2 >> i) & 1)
          inSensorReading[gate] = HIGH;
      else inSensorReading[gate] = LOW;      
      gate++;  
    }
    for(int i = 0; i < 8; i++)
    {
      if((switchBank3 >> i) & 1)
          outSensorReading[gate] = HIGH;
      else outSensorReading[gate] = LOW;
      i++;
      if((switchBank3 >> i) & 1)
          inSensorReading[gate] = HIGH;
      else inSensorReading[gate] = LOW;       
      gate++;  
    }
    for(int i = 0; i < 8; i++)
    {
      if((switchBank4 >> i) & 1)
          outSensorReading[gate] = HIGH;
      else outSensorReading[gate] = LOW;
      i++;
      if((switchBank4 >> i) & 1)
          inSensorReading[gate] = HIGH;
      else inSensorReading[gate] = LOW;       
      gate++;  
    }
    for(int i = 0; i < 8; i++)
    {
      if((switchBank5 >> i) & 1)
          outSensorReading[gate] = HIGH;
      else outSensorReading[gate] = LOW;
      i++;
      if((switchBank5 >> i) & 1)
          inSensorReading[gate] = HIGH;
      else inSensorReading[gate] = LOW;       
      gate++;  
    }
    for(int i = 0; i < 8; i++)
    {
      if((switchBank6 >> i) & 1)
          outSensorReading[gate] = HIGH;
      else outSensorReading[gate] = LOW;
      i++;
      if((switchBank6 >> i) & 1)
          inSensorReading[gate] = HIGH;
      else inSensorReading[gate] = LOW;      
      gate++;  
    }  
    oldSwitchBank1 = switchBank1;
    oldSwitchBank2 = switchBank2;
    oldSwitchBank3 = switchBank3;
    oldSwitchBank4 = switchBank4;
    oldSwitchBank5 = switchBank5;
    oldSwitchBank6 = switchBank6;
  }

  for (int i = startGate; i < endGate; i++) 
  { 
    if(inSensorReading[i] == HIGH || outSensorReading[i] == HIGH) 
    {
      digitalWrite(testLed, HIGH);
      break;
    }
    digitalWrite(testLed, LOW);
  }
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

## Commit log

2020-02-22 updated SIP 22ohm resistors to qty(4)
2020-03-15 version1
    updated with version 1 Feather only and kicad design files
    [easy_bee_Itsybitsy.brd, easy_bee_Itsybitsy.sch, easy_bee_feather_route.brd, easy_bee_feather_route.sch]
2020-03-15 still working on PCB files
2020-03-16 updated code with itsybitsy power pins
2020-03-17 updated blinking IR leds
2020-03-17 add instructions video
    [easy_bee_counter.brd, easy_bee_counter.sch]
2020-03-23 Converted Bee Logo into an Eagle Part
    Here's a library containing a single device which has 1 symbol and 1 package.
    The symbol is a simple rectangle that shows up in the schematic and says "Bee Logo".
    Adding the device in the schematic editor will create a copy of the image in the schematic which can be grabbed by the Anchor at the lower left corner and easily moved around for placement on the PCB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
    The Bee Logo itself is in the TPlace layer (as was the original Bee Logo). The anchor for dragging it around is in the Reference layer so that the anchor doesn't get printed on the actual silk screen.
    Mirroring the logo will automatically move it to the BPlace layer as well.
2020-03-30 Converted Logo to library part Added vias to be solded bridged for jumpers to bypass the SIP resistors. Rerouted the board, realigned many of the parts.
    [easy_bee_counter.brd, easy_bee_counter.sch]
2020-03-30 Added jumpers for 13-24 (oops). Added Tkeepout areas to expose jumpers on component side.
    [easy_bee_counter.brd]
2020-03-30 cleaned up some additional errors.
    [easy_bee_counter.brd]
2020-04-25 added kiCad_files
    [easy_bee_feather_route.kicad_pcb, easy_bee_feather_route.sch]
2020-04-25 added gerbers
    [easy_bee_feather_route-B_Mask.gbr, easy_bee_feather_route-B_SilkS.gbr, easy_bee_feather_route-Bottom.gbr, easy_bee_feather_route-Edge_Cuts.gbr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]
2020-05-01 re-output gerber files
    JLCPCB indicated in an email that something was wrong with the gerber files. Seemed to upload fine. OSHPark said they were missing the copper layer which was strange.. Re-output gerber files based on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
    [easy_bee_feather_route-B_Mask.gbs, easy_bee_feather_route-B_SilkS.gbo, easy_bee_feather_route-Bottom.gbl, easy_bee_feather_route-Edge_Cuts.gm1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]
2020-05-20 note on using the esp8266
    pin A5 is missing!
2020-07-21 added python sample code
2021-03-01 Update README.md
    updated the readMe detailing issues with the 74HC165 not being a true SPI device
2024-03-07 Update README.MD
    The GERBER files were developed from the kicad board files so had to remove the gerber files. You now have to use the Eagle board files or generate gerber files from the eagle board files.
    https://github.com/hydronics2/2019-easy-bee-counter/issues/25
2024-03-07 Update README.md
    The GERBER files were developed from the kicad board files so had to remove the gerber files. You now have to use the Eagle board files or generate gerber files from the eagle board files.... or a lo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
2024-03-07 Delete PCB_files/gerbers2.zip
    The GERBER files were developed from the kicad board files and there was a small error in the kiCAD files... so the gerber files have been removed. You now have to use the Eagle board files or genera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
2024-03-07 Delete PCB_files/Kicad_v/gerbers directory
    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
    [easy_bee_feather_route-B_Mask.gbs, easy_bee_feather_route-B_SilkS.gbo, easy_bee_feather_route-Bottom.gbl, easy_bee_feather_route-Edge_Cuts.gm1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]
2024-03-07 Create read.me
    There is a small error in the kiCAD files... You now have to use the Eagle board files or generate gerber files from the eagle board files.... or a lot of PCB manufacturers will take eagle PCB files 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

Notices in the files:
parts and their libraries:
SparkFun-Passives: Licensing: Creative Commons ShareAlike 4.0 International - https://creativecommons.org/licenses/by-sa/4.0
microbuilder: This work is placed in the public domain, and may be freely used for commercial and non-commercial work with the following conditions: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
